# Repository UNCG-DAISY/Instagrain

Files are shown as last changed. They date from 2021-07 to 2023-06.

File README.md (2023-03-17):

# Instagrain

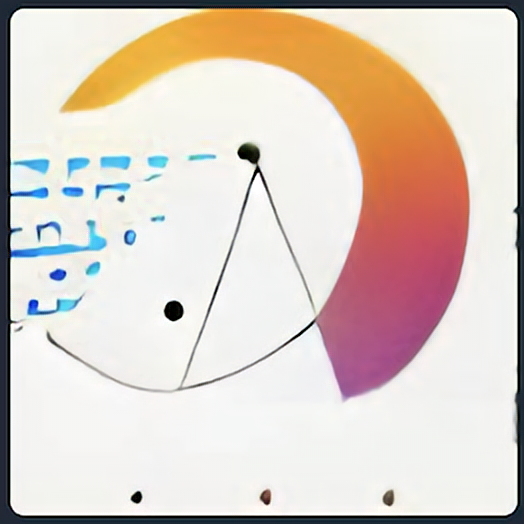
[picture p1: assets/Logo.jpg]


[](
https://github.com/UNCG-DAISY/SandCam/commits/main)












A camera for measuring sediment grain size in the field - ['instant grainification'](https://ui.adsabs.harvard.edu/abs/2007AGUFM.H51I0899R/abstract) (h/t Rubin & Chezar, 2007)
The camera currently runs a deep learning model to estimate grain size from pictures (using tensorflow lite)

We have several working prototypes out in the field. Here at HQ we continue to refine the camera design, hardware, software, and ML model. 

Prototype 1 (3D printed case)

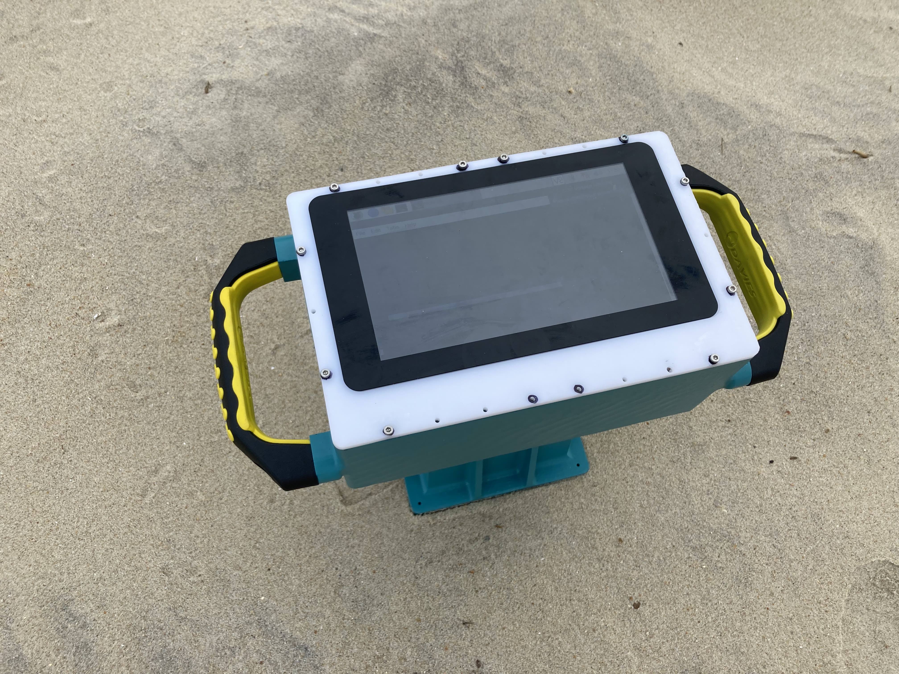
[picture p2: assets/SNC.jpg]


Prototype 2 (current version; CNC'ed case and 3D printed parts)

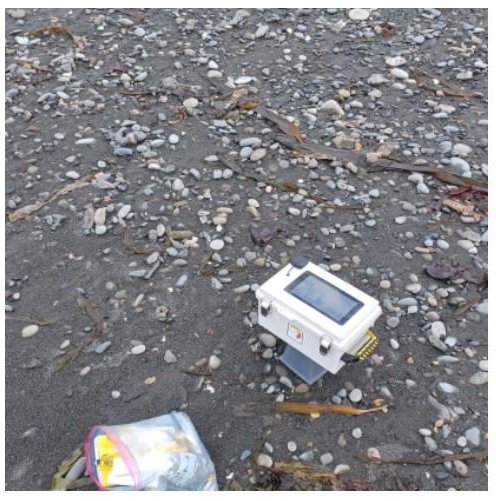
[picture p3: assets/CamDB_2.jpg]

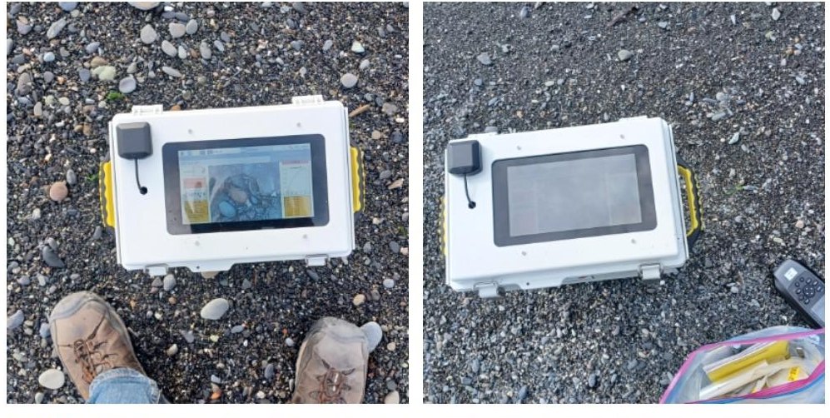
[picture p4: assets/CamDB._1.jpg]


## Do you want to be involved?:

0. Get in touch with us, we would be happy to collaborate!

1. Check out our [wiki](https://github.com/UNCG-DAISY/Instagrain/wiki) to learn how to build and use the camera.  

2. Read through the repository to look at the files/code we provide.

3. Check out the open [issues](https://github.com/UNCG-DAISY/Instagrain/issues) and participate in our [discussion](https://github.com/UNCG-DAISY/Instagrain/discussions). 

## Code of Conduct:

We intend to foster an inclusive and respectful environment surrounding the contribution and discussion of our project. Make sure you understand our [Code of Conduct](./CODE_OF_CONDUCT.md).

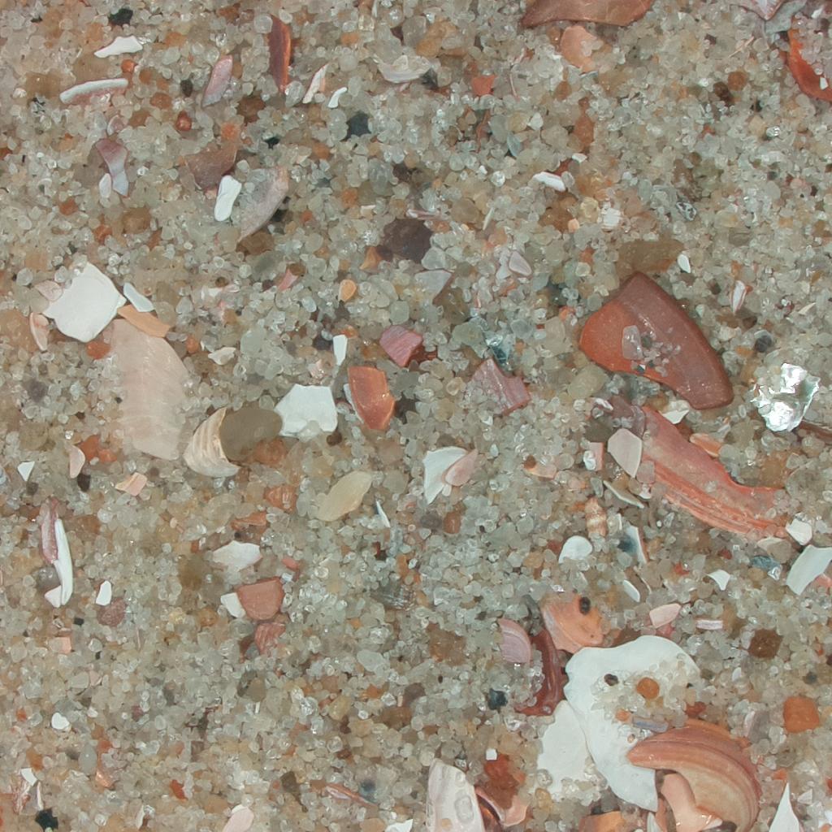
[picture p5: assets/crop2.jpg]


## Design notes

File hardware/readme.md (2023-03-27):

# This is the hardware folder

** please refer to the Wiki for instructions on how to build the device **

There are multiple versions of both the camera case and the electronics/hardware.

V1: The Case is fully 3d printed. We strongly recommend using an SLA printer. We have verified this model works with a FormLab 3+ using grey pro resin.

V2: This new case is a custom CNC'ed polycase enclosure and a few 3D printed parts. Again we recommend an SLA printer (we used a Formlab 3/3+ and Grey pro resin), but have heard of success using an FDM printer. There are mounting holes for an (optional) Google Coral edgeTPU, the GPS is provided by an Adafruit GPS hat connected to an external antenna (via an adaptor). 

V3: A smaller custom CNC'ed polycase enclosure, with fewer mounting points, and iterating on some design choices. Again there are a few 3D printed parts, and we recommend an SLA printer (we used a Formlab 3/3+ and Grey pro resin), but have heard of success using an FDM printer. The mounting holes for the Google Coral edgeTPU are eliminated, we switched to a USB GPS to simplify the BOM/parts list.

Notes:
- All `.stp` files can be viewed using [Autodesk Viewer](https://viewer.autodesk.com)
- The camera tent is interchangeable between V2 and V3, as is the ring light holder. (but the screen brackets are different between V2 and V3)

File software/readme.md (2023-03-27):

# This is the software folder

** please refer to the Wiki for instructions on how to set up the software on the device **

There are multiple versions of the case and hardware for hte camera, and we provide here matching versions of the software for each hardware configuration.

The software for the v1 and v2 camera are in the the `v2_and_v1` folder. This is software for the fully 3D printed camera and the larger (v2) custom CNC'ed polycase enclosure. This runs on Raspbian 'Buster', and uses Picamera 

The software for the v3 camera (smaller polycase enclosure) is provided in the `v3` folder. This runs on Raspbian 'Buster', and uses the Picamera library.

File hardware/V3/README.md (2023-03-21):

# Camera hardware readme for v3

** please note that there are multiple versions of both the camera case and the electronics/hardware. **

You are looking at V3, where the case is a smaller custom CNC'ed polycase enclosure and a few 3D printed parts. We recommend an SLA printer (we used a Formlab 3/3+ and Grey pro resin), but have heard of success using an FDM printer. 

### BOM v3

Full List of Materials can be found on the BOMv3.csv, (currently a rough draft)

---
### Major Components

- Most of the major Components can be ordered from our Adafruit wishlist http://www.adafruit.com/wishlists/561634 additionally there is Digikey links available in the [`BOMv3.csv`]  
  - The recommended microSD card can be bought on Amazon https://www.amazon.com/SanDisk-Extreme-microSDHC-UHS-3-SDSQXAF-032G-GN6MA/dp/B06XWMQ81P/
  - Due to chip shortages in 2021 and 2022, the Raspberry Pi 4 may not be available on Adafruit
- There are two STEP files that can be sent to Polycase* to order the custom-designed, CNC-machined camera housing (expect 1 to 3 week lead time). Polycase should alread have the "setup" complete, which reduces the overall unit cost. 
  - WQ-50_BODY.step
  - WQ-50_LID.stp
  - WQ-50_BASEPLATE.stp

*Instructions for sending requests for custom CNC-machined parts are available at https://www.polycase.com/customized-enclosures 

---
### Hardware

The fastener hardware can be ordered from a Mcmaster-Carr cart https://www.mcmaster.com/order/rcvRtedOrd.aspx?ordid=9740526925745&lnktyp=txt

---
### 3D Parts

There are four `.stl` files
- [`Camcover.stl`](./Camcover.stl)
- [`screenbracketsmaller.stl`](./screenbracketsmaller.stl)
- [`ledmountv2.stl`](./ledmountv2.stl)
- [`focuscover.stl`](./focuscover.stl)

We recommend printing all of them with a SLA printer with a build volumne of 14.5 × 14.5 × 18.5 cm and using grey pro resin.

Printing takes roughly 44.45hrs with a Form3/3+ printer (Look at [`BOMv3.csv`](./BOMv3.csv) for full part breakdown)

---

# Wiring Diagram

To assemble the camera, you will need the parts described in the bill of materials — [`BOMv3.csv`](./BOM.csv). 

A wiring diagram is available in Fritzing format — [`sandcamv2.fzz`](./sandcamv2.fzz).



---

# Build Instructions 

---

### Tools Needed 
- Soldering Iron
- Soldering Wire
- Flux
- Wire Strippers
- Metric Hex Bit Set
- Imperial Allen Key Set

### Components 
The Build Process is Broke down into 8 major parts:
- Soldering the Adafruit Ultimate GPS Hat and Neopixel board
- Mounting the Screen 
- Camera Assembly 
- Installing Handles
- Base Plate Assembly 
- Final assembly
- Focusing the Camera

---

 ### Step 1 --- Soldering 
First solder the GPIO header to the Adafruit ultimate GPS hat  


Next cut three, 8in male to female jumper cables in half, red for 5v, black for ground, and purple for data  
  

Once the wires are cut strip off about 5mm from each wire similar to how it is done in the above picture
and then twist the ends of the wires together and tin them  

 
Now we will solder the female ends to the Neopixel board, make sure solder the red wire to the middle 5v, the black wire to the middle GND, and the purple wire to the data input, so that the [`ledmountv2.stl`](./ledmountv2.stl) fits 


Next solder the male ends to the Adafruit Ulimate GPS Hat, the red wire to the 5v strip, the black to the GND strip, and the purple wire to GPIO #8 
Tip: I recommend soldering the 5v and GND at different ends (Differenly then I did in the picture below)



For the final step place the Neopixel Light into the [`ledmountv2.stl`](./ledmountv2.stl) 


---

### Step 2 --- Mounting the Screen
For this step, four 8mm M3 socket head screws, four 12mm M2.5 socket head screws, and four M2.5 hex nuts are needed
First start the four M3 Socket Head Screws into the two mounting holes in the center of the [`screenbracket.stl`](./screenbracket.stl) 
(will have a picture here soon)

Next attach the Brackets to the polycase with the four 12mm M2.5 socket head screws and the four M2.5 hex nuts



Once attached place the screen face down with the larger bezel on the left 


Finish by putting the outside of the polycase lid to the backside of the Screen and tightem the M3 socket head screws to the screen till the screen is flush with the front of the polycase  



---

### Step 3 --- Mounting the Coral TPU
Mounting the Coral TPU uses four 10mm M2.5 female to female hex standoffs, four 12mm M2.5 socket head screws, and four 6mm M2.5 socket head screws  
This is a fairly starightforward step, for now we recommend it is mounted on the outside until tempature testing can be done with the Coral TPU on the inside


### Step 4 --- Camera Assembly
For this step you will need eight 16mm female to male standoffs, four 2.5mm hex nuts, and four 6mm M2.5 socket head screws  
For the purpose of focusing the Pi HD camera you will need to disassemble and remove this part

The removed part and pi HD camera will now look like this

Next attach 4 standoffs to the bottom of the camera and then 4 between the neopixel light and the top of the pi camera



Finally attach the the camera to the outside of the case with the four 6mm M2.5 socket head bolts



---

### Step 5 --- Mounting the Handles
For this step you will need four quarter inch bolts and four quarter inch lock nuts  




---

### Step 6 --- Base Plate Assembly
For this step you will need two ribbon cables, four 10mm female to male standoffs, four 11mm female to male standoffs, a velcro strap, four M2.5 hex nuts, and four 6mm M2.5 socket head screws     
First step is to attach the two ribbon cables to the Raspi, for the screen and the camera  


Next attach the adafruit ultimate GPS hat with the black 11mm standoffs, then attach the 10mm standoffs to the bottom of the pi    



Secure the Raspi assembly to the baseplate with the four 6mm M2.5 socket head screws, and then secure the battery to the baseplate with the velcro strip


Finally secure the baseplate in the bottom of the case with the four screws that come with the polycase


---

### Step 7 --- Final Assembly
Thread the GPS antenna through the hexagonal hole in the front of the case annd attach wih double sided tape or glue to the outside of the case   


Next pull the camera ribbon through the slotted hole in the bottom of the case, and then connect the jumper cables


Connect the ground and 5v jumper cable to the screen, and connect the display ribbon to the screen


Connect the GPS to the adafruit ultimate GPS hat and zip tie in place to secure



For the final step plug in the battery to the on/off button, the on/off button to the Raspi, and then the coral TPU to the Pi


---

### Step 8 --- Focusing the Camera 
This is by far the hardest step, it is recommended to disconnect the screen and plug the raspi into a larger screen via hdmi   
First remove the [`Camcover.stl`](./Camcover.stl) and attach the [`focuscover.stl`](./focuscover.stl) which allows for better access to the camera 
Boot up the raspi and run the [`preview.py`](./preview.py) script
Focus the camera by twisting the HD lens  (this step might take a while), it is recommened to keep a small apeture for a large depth of focus  
Once the camera is in focus tighten down all the camera screws and place the [`Camcover.stl`](./Camcover.stl) on the case by inserting the pegs and twisting

Finally the touch screen can be hooked back up and the Sandcam is now ready to work
(pictures coming soon)

---

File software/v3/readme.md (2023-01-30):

# Setting up the camera software on the Pi

After assembling the case and wiring the electronics for the RPi (see the ['hardware directory'](../hardware)), it's time to get the Software and configurations set.

By default the camera runs a deep learning model, but can also run [pyDGS](https://github.com/dbuscombe-usgs/pyDGS) — software written by [Dan Buscombe](https://github.com/dbuscombe-usgs) that estimates grain size distribution (percent finer) of an image using the continuous wavelet transform.

## Option 1
Flash sd card with image from https://cshl.synology.me:5001/d/f/670216654824718296   

## Option 2
## Update Pi 

Boot up Raspberry Pi and connect to internet, and update Raspberry Pi with commands
```
sudo apt-get update
sudo apt-get upgrade
sudo reboot
```

## Configure Pi

Applications menu -> Preferences -> Raspberry Pi Configuration -> Interfaces -> ENABLE; Camera, SPI,(SSH, VNC are optional)  
`sudo reboot` 

## Add Hardware

After reboot  
Power Raspi off and add header extension, attach GPS to UART pins. Place RTC on I2C.
Connect Pi HQ camera to raspberry pi  

Connect Button to GPIO26 and to GND 
Connect LED light to GPIO18, 5v (back of RTC), and GND  
Power Raspberry pi on   

## Install the Pandas Package   
`pip3 install pandas`   

## Install the MatPlotLib Package
`sudo pip3 install maplotlib`

## Install scipy
`sudo apt-get install libatlas-base-dev`

`pip3 install scipy`

## set up GPS

`sudo raspi-config`    
interfacing options (3) -> Serial Port (P6) -> No -> Yes -> Finish   
then reboot   

Install, gpsd, gpsmon and cgps  
`sudo apt-get install gpsd-clients gpsd -y`

config GPS to work with correct serial device  
`sudo nano /etc/default/gpsd`  
Look for  `DEVICES=""`  
Change to `DEVICES="/dev/serial0"`  
Now save file (control X, Y) 
`pip3 install gpsd-py3` to download gps for python3


## set up RTC

`sudo raspi-config` Interface options (3) -> (P5) I2C -> yes -> finish  




  
`sudo reboot`  
Now use i2cdetect to see if the RTC is working   
`sudo i2cdetect -y 1` will show mounted drives, you should see a 68  
  
`sudo nano /boot/config.txt`        
Add to the end    
`#rtc`   
`dtoverlay=i2c-rtc,ds3231`     
save and exit (control x, y, enter)   
  
Now that we have the RTC ready to work on boot, restart your pi and..
`sudo i2cdetect -y 1` a mounted drive will have a "UU" ID  
   
Setting up RTC to be the main clock  
First disable the fake "hwclock"   
`sudo apt-get -y remove fake-hwclock`   
`sudo update-rc.d -f fake-hwclock remove`      
`sudo systemctl disable fake-hwclock`     

Second make the RTC to the main clock   
Run `sudo nano /lib/udev/hwclock-set` and comment out the following lines with `#`   
`if [-e/run/systemd/system];then`   
`exit 0`    
`fi`     
   
`/sbin/hwclock --rtc=$dev --systz --badyear`   

`/sbin/hwclock --rtc=$dev --systz`   
    

Make sure there is an internet connection so that the clocks can sync

## set up Neopixel Lite   
`sudo pip3 install rpi_ws281x adafruit-circuitpython-neopixel`   

## set up Tensorflow Lite

Follow instructions to `pip install` the tflite runtime on the Raspberry Pi
https://www.tensorflow.org/lite/guide/python

create a `/models/` directory on the desktop and place the `*.tflite` file (the tflite model) in that directory.

## set up Google Coral TPU (Optional)  
Run the commands   
`echo "deb https://packages.cloud.google.com/apt coral-edgetpu-stable main" | sudo tee /etc/apt/sources.list.d/coral-edgetpu.list`   
`curl https://packages.cloud.google.com/apt/doc/apt-key.gpg | sudo apt-key add -`   
`sudo apt-get update`   

Next Install Edge TPU Runtime
`sudo apt-get install libedgetpu1-std`   

Now Install the Pycoral Library   
`sudo apt-get install python3-pycoral`   

The Google Coral is ready to be plugged in now  
To test use the code below   
`mkdir coral && cd coral`   
`git clone https://github.com/google-coral/pycoral.git`   
`cd pycoral`   

`bash examples/install_requirements.sh classify_image.py`   

`python3 examples/classify_image.py \`  
`--model test_data/mobilenet_v2_1.0_224_inat_bird_quant_edgetpu.tflite \`  
`--labels test_data/inat_bird_labels.txt \`  
`--input test_data/parrot.jpg` 

The outtput should look something like the screenshot below, if it is not working restart Pi and try this section again, it has been finicky for me



## set up pyDGS (optional)
visit https://github.com/dbuscombe-usgs/pyDGS to look pyDGS or download to pi with `git clone --depth 1 https://github.com/dbuscombe-usgs/pyDGS.git`  
once downloaded edit test.py script to look like example code in SandCam --> camerasoftware --> pyDGS --> example_test.py  
next copy the __pycache__ folder, dgs.pyc, and dgs.py to your SandCam folder 

--- 

Helpful instructions to get packages for Ring LED, GPS, Coral TPU, and RTC  
https://www.thegeekpub.com/16187/controlling-ws2812b-leds-with-a-raspberry-pi/  
https://ozzmaker.com/berrygps-setup-guide-raspberry-pi/  
https://coral.ai/docs/accelerator/get-started#1-install-the-edge-tpu-runtime   
https://maker.pro/raspberry-pi/tutorial/how-to-add-an-rtc-module-to-raspberry-pi  

## Usage
When the Raspi is booted up, double click on the RUN.sh script  
Once the GUI is booted up you will see two buttons, preview and shutter  
Preview will show a live preview of the camera, make sure there is no large shells, sticks, or debry 
Photos and a text file will be stored in a new folder with the date and time, the text file will have every photo with the time taken, corresponding GPS coordinates, altitude, and grain size percentiles  

NOTE: -9999 under lat, lon, and alt means the GPS can not get a lock on coordinates. For best GPS results use external GPS.  

photos  
 
cropped photos  
  
Example text file  


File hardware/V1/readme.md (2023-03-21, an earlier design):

# Camera hardware readme for v1

** please note that there are multiple versions of both the camera case and the electronics/hardware. **

You are looking at V1, where the Case is fully 3d printed. We strongly recommend using an SLA printer. We have verified this model works with a FormLab 3+ using grey pro resin.

----

This directory addresses two aspects of the camera: 

- the 3D printed case of tha camera
- the electronic assembly of the camera. 

## 3D Printed case

There are 5 `.stl` files 

1. [Camera body](./body_sedicamsmallerv2.stl)
2. [Light mount](./lightmount.stl)
3. [Battery case](./battery_case.stl)
4. [Screen Mount](./screen_mount.stl)
5. [USB Door](./usbdoor_sedicam.stl)

We recommend printing all of them with a SLA printer with a build volumne of XXX and using rigid resin.

Printing takes roughly XXX with a XXX printer

Instructions for assembly are forthcoming.

---
# Wiring diagram 

To assemble the camera, you will need the parts described in the bill of materials — [`BOM.md`](./BOM.md). 

A wiring diagram is available in Fritzing format — [`SediNetCamv2.fzz`](./SediNetCamv2.fzz). 

Instructions for assembly are forthcoming.



---

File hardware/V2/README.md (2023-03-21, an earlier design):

# Camera hardware readme for v2

** please note that there are multiple versions of both the camera case and the electronics/hardware. **

You are looking at V2, where the case is a custom CNC'ed polycase enclosure and a few 3D printed parts. We recommend an SLA printer (we used a Formlab 3/3+ and Grey pro resin), but have heard of success using an FDM printer. 

# BOM v2

Full List of Materials can be found on the [`BOMv2.csv`](./BOMv2.csv)

---
### Major Components

- Most of the major Components can be ordered from our Adafruit wishlist http://www.adafruit.com/wishlists/543790 additionally there is Digikey links available in the [`BOMv2.csv`](./BOMv2.csv)
  - The Google Coral can be found at https://coral.ai/products/accelerator  
  - The recommended microSD card can be bought on Amazon https://www.amazon.com/SanDisk-Extreme-microSDHC-UHS-3-SDSQXAF-032G-GN6MA/dp/B06XWMQ81P/
  - Due to chip shortages in 2021 and 2022, the Raspberry Pi 4 may not be available on Adafruit
- There are two STEP files that can be sent to Polycase* to order the custom-designed, CNC-machined camera housing (expect 1 to 3 week lead time). Polycase should alread have the "setup" complete, which reduces the overall unit cost. 
  - WQ-57C_LID.stp
  - WQ-57_Body.stp

*Instructions for sending requests for custom CNC-machined parts are available at https://www.polycase.com/customized-enclosures 

---
### Hardware

The fastener hardware can be ordered from a Mcmaster-Carr cart https://www.mcmaster.com/order/rcvRtedOrd.aspx?ordid=2837271750220&lnktyp=txt 

---
### 3D Parts

There are four `.stl` files
- [`Camcover.stl`](./Camcover.stl)
- [`screenbracket.stl`](./screenbracket.stl)
- [`ledmountv2.stl`](./ledmountv2.stl)
- [`focuscover.stl`](./focuscover.stl)

We recommend printing all of them with a SLA printer with a build volumne of 14.5 × 14.5 × 18.5 cm and using rigid resin.

Printing takes roughly 44.45hrs with a Form3/3+ printer (Look at [`BOMv2.csv`](./BOMv2.csv) for full part breakdown)

---
### CNC Part

There is only one part that needs to be custom made or hand machined
- [`WQ-57P-01.pdf`](./WQ-57P-01.pdf)

The above file has all the necessary dimensions for hand machining, feel free to make any improvements and share!

---

# Wiring Diagram

To assemble the camera, you will need the parts described in the bill of materials — [`BOMv2.csv`](./BOM.csv). 

A wiring diagram is available in Fritzing format — [`sandcamv2.fzz`](./sandcamv2.fzz).



---

# Build Instructions 

---

### Tools Needed 
- Soldering Iron
- Soldering Wire
- Flux
- Wire Strippers
- Metric Hex Bit Set
- Imperial Allen Key Set

### Components 
The Build Process is Broke down into 8 major parts:
- Soldering the Adafruit Ultimate GPS Hat and Neopixel board
- Mounting the Screen
- Coral mounting 
- Camera Assembly 
- Installing Handles
- Base Plate Assembly 
- Final assembly
- Focusing the Camera

---

 ### Step 1 --- Soldering 
First solder the GPIO header to the Adafruit ultimate GPS hat  


Next cut three, 8in male to female jumper cables in half, red for 5v, black for ground, and purple for data  
  

Once the wires are cut strip off about 5mm from each wire similar to how it is done in the above picture
and then twist the ends of the wires together and tin them  

 
Now we will solder the female ends to the Neopixel board, make sure solder the red wire to the middle 5v, the black wire to the middle GND, and the purple wire to the data input, so that the [`ledmountv2.stl`](./ledmountv2.stl) fits 


Next solder the male ends to the Adafruit Ulimate GPS Hat, the red wire to the 5v strip, the black to the GND strip, and the purple wire to GPIO #8 
Tip: I recommend soldering the 5v and GND at different ends (Differenly then I did in the picture below)



For the final step place the Neopixel Light into the [`ledmountv2.stl`](./ledmountv2.stl) 


---

### Step 2 --- Mounting the Screen
For this step, four 8mm M3 socket head screws, four 12mm M2.5 socket head screws, and four M2.5 hex nuts are needed
First start the four M3 Socket Head Screws into the two mounting holes in the center of the [`screenbracket.stl`](./screenbracket.stl) 
(will have a picture here soon)

Next attach the Brackets to the polycase with the four 12mm M2.5 socket head screws and the four M2.5 hex nuts



Once attached place the screen face down with the larger bezel on the left 


Finish by putting the outside of the polycase lid to the backside of the Screen and tightem the M3 socket head screws to the screen till the screen is flush with the front of the polycase  



---

### Step 3 --- Mounting the Coral TPU
Mounting the Coral TPU uses four 10mm M2.5 female to female hex standoffs, four 12mm M2.5 socket head screws, and four 6mm M2.5 socket head screws  
This is a fairly starightforward step, for now we recommend it is mounted on the outside until tempature testing can be done with the Coral TPU on the inside


### Step 4 --- Camera Assembly
For this step you will need eight 16mm female to male standoffs, four 2.5mm hex nuts, and four 6mm M2.5 socket head screws  
For the purpose of focusing the Pi HD camera you will need to disassemble and remove this part

The removed part and pi HD camera will now look like this

Next attach 4 standoffs to the bottom of the camera and then 4 between the neopixel light and the top of the pi camera



Finally attach the the camera to the outside of the case with the four 6mm M2.5 socket head bolts



---

### Step 5 --- Mounting the Handles
For this step you will need four quarter inch bolts and four quarter inch lock nuts  




---

### Step 6 --- Base Plate Assembly
For this step you will need two ribbon cables, four 10mm female to male standoffs, four 11mm female to male standoffs, a velcro strap, four M2.5 hex nuts, and four 6mm M2.5 socket head screws     
First step is to attach the two ribbon cables to the Raspi, for the screen and the camera  


Next attach the adafruit ultimate GPS hat with the black 11mm standoffs, then attach the 10mm standoffs to the bottom of the pi    



Secure the Raspi assembly to the baseplate with the four 6mm M2.5 socket head screws, and then secure the battery to the baseplate with the velcro strip


Finally secure the baseplate in the bottom of the case with the four screws that come with the polycase


---

### Step 7 --- Final Assembly
Thread the GPS antenna through the hexagonal hole in the front of the case annd attach wih double sided tape or glue to the outside of the case   


Next pull the camera ribbon through the slotted hole in the bottom of the case, and then connect the jumper cables


Connect the ground and 5v jumper cable to the screen, and connect the display ribbon to the screen


Connect the GPS to the adafruit ultimate GPS hat and zip tie in place to secure



For the final step plug in the battery to the on/off button, the on/off button to the Raspi, and then the coral TPU to the Pi


---

### Step 8 --- Focusing the Camera 
This is by far the hardest step, it is recommended to disconnect the screen and plug the raspi into a larger screen via hdmi   
First remove the [`Camcover.stl`](./Camcover.stl) and attach the [`focuscover.stl`](./focuscover.stl) which allows for better access to the camera 
Boot up the raspi and run the [`preview.py`](./preview.py) script
Focus the camera by twisting the HD lens  (this step might take a while), it is recommened to keep a small apeture for a large depth of focus  
Once the camera is in focus tighten down all the camera screws and place the [`Camcover.stl`](./Camcover.stl) on the case by inserting the pegs and twisting

Finally the touch screen can be hooked back up and the Sandcam is now ready to work
(pictures coming soon)

---

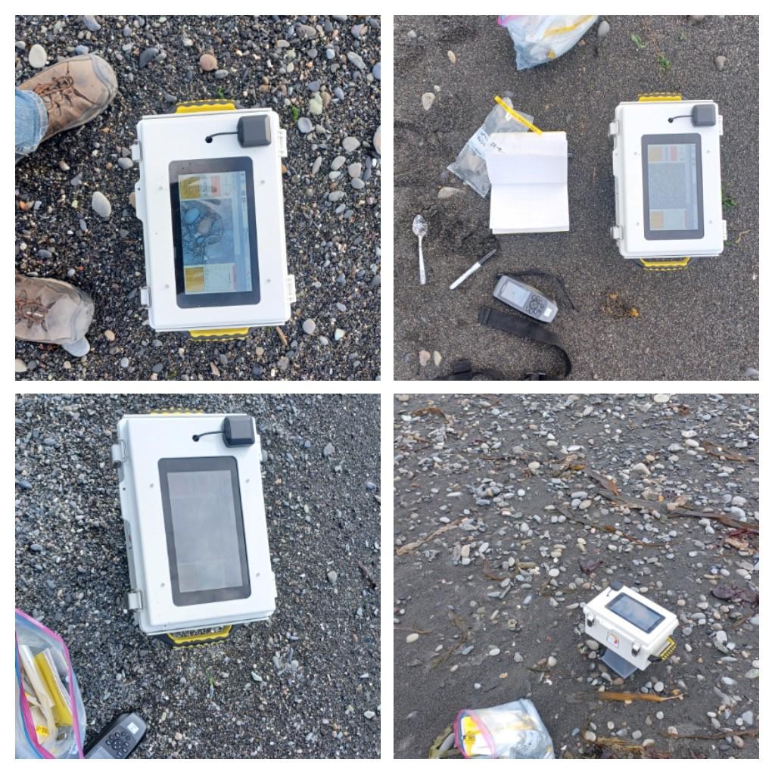
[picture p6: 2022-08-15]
assets/CamDB.jpg

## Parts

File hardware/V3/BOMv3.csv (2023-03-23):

OM SandCam V2
Major Components
Item | Price per Unit | Manufactuer | Procurment Type | ID Number | Link
Polycase WQ-50 (per unit, assuming order is 5 parts) | $133.65 | Polycase | CNC | NA | NA
Polycase WQ-50 Baseplate (per unit, assuming order is 5 parts) | $21.52 | Polycase | CNC | WQ-57P-01 | https://www.polycase.com/wq-50p
Raspberry Pi 4 Model B - 2 GB RAM | $45.00 | Adafruit | Off-The-Shelf | 4292 | https://www.adafruit.com/product/4292
SanDisk 32GB Micro SD card | $10.19 | Amazon | Off-The-Shelf | NA | https://www.amazon.com/SanDisk-Extreme-microSDHC-UHS-3-SDSQXAF-032G-GN6MA/dp/B06XWMQ81P |  |  | .
6mm 3MP Wide Angle Lens for Raspberry Pi HQ Camera - 3MP | $25.00 | Adafruit | Off-The-Shelf | 4563 | https://www.adafruit.com/product/4563
Raspberry Pi High Quality HQ Camera - 12MP | $50.00 | Adafruit | Off-The-Shelf | 4561 | https://www.adafruit.com/product/4561
USB Battery Pack for Raspberry Pi - 10000mAh - 2 x 5V outputs | $39.95 | Adafruit | Off-The-Shelf | 1566 | https://www.adafruit.com/product/1566
Pi Foundation Display - 7" Touchscreen Display for Raspberry Pi | $79.95 | Adafruit | Off-The-Shelf | 2718 | https://www.adafruit.com/product/2718
VK-162 G-Mouse - Remote Mount USB - External GPS Navigation Dongle | $19.99 | Amazon | Off-The-Shelf | NA | https://www.amazon.com/gp/product/B01EROIUEW
NeoPixel Ring - 24 x 5050 RGB LED with Integrated Drivers | $16.95 | Adafruit | Off-The-Shelf | 1586 | https://www.adafruit.com/product/1586
Total Component Costs | $442.20
3D printable Components
Item | Length | Width | Height | Recommended Printer | Recommended Resin | Volume/Print Time/Layers | Link
Camera Hood | 126mm | 126mm | 138.8mm | Form 3/3+ | Grey Pro | 310ml/30.5 hrs/1647 | https://github.com/UNCG-DAISY/SandCam/blob/main/hardware/V2/Camcover.stl
Screen Bracket | 140mm | 10mm | 12.6mm | Form 3/3+ | Grey Pro | 34.2ml/8.5 hrs/858 | https://github.com/UNCG-DAISY/SandCam/blob/main/hardware/V2/screenbracket.stl
LED Mount | 74mm | 74mm | 4mm | Form 3/3+ | Grey Pro | 9.74ml/5.45 hrs/659 | https://github.com/UNCG-DAISY/SandCam/blob/main/hardware/lightmount.stl
Focus Hood | 114mm | 114mm | 138.8mm | Form 3/3+ | Grey Pro | 46.44ml/14 hr/1472 | https://github.com/UNCG-DAISY/SandCam/blob/main/hardware/V2/focuscover.stl
Hardware
Item | Size | Length | Quantity | Unit of Measure | Unit Price | Total Cost | Manufacturer | Item Number | Webiste
18-8 Stainless Steel Socket Head Screw | M2.5 | 12mm | 8 | 1 pack of 100 each | $6.54 | $6.54 | McMaster-Carr | 91292A016
Stainless Steel Female Hex Standoff | M2.5 | 10mm | 4 | each | $1.32 | $5.28 | McMaster-Carr | 94868A165
Stainless Steel Male Hex Standoff | M2.5 | 16mm | 8 | each | $4.82 | $38.56 | McMaster-Carr | 93655A353
18-8 Stainless Steel Socket Head Screw | M2.5 | 6mm | 12 | 1 pack of 100 each | $6.00 | $6.00 | McMaster-Carr | 91292A010
18-8 Stainless Steel Socket Head Screw | M3 x 0.5mm | 8mm | 4 | 1 pack of 100 each | $5.45 | $5.45 | McMaster-Carr | 91292A112
18-8 Stainless Steel Socket Head Screw | 1/4" - 20 | 1.25" | 4 | 1 pack of 25 each | $17.51 | $17.51 | McMaster-Carr | 92196A544
Plastic Unthreaded-Hole Rectangular Pull Handle | 3-11/16 | NA | 2 | each | $4.24 | $8.48 | McMaster-Carr | 1078A311
Stainless Steel Male Hex Standoff | M2.5 | 10mm | 4 | each | $4.26 | $17.04 | McMaster-Carr | 93655A096
Brass M2.5 Standoffs for Pi HATs - Black Plated - Pack of 2 | M2.5 | 11mm | 4 | 1 pack of 2 each | $0.75 | $1.50 | AdaFruit | 2336 | https://www.adafruit.com/product/2336 | .
Female/Male Jumper Wires | NA | 6" | 5 | 20 | $1.95 | $1.95 | AdaFruit | 1954 | https://www.adafruit.com/product/1954
Metric 18-8 Stainless Steel Hex Nuts | M2.5 | NA | 12 | 1 pack of 100 each | $7.18 | $7.18 | McMaster-Carr | 91828A113
18-8 Stainless Steel Hex Nuts | 1/4" - 20 | NA | 4 | 1 pack of 100 each | $7.16 | $7.16 | McMaster-Carr | 91845A029
Long-Lasting Cable Ties | Narrow | 4" |  | 1 pack of 100 each | $8.60 | $8.60 | McMaster-Carr | 70215K61
316 Stainless Steel Washers | 1/4" | NA | 4 | 1 pack of 100 each | $10.01 | $10.01 | McMaster-Carr | 90107A029
18-8 Stainless Steel Washers | M2.5 | NA | 12 | 1 pack of 100 each | $2.86 | $2.86 | McMaster-Carr | 98689A111
20-inch camera ribbon | NA | 20" | 1 | 1 | $5.19 | $5.19 | Amazon | NA | https://www.amazon.com/dp/B07JZHD614/ref=cm_sw_r_apan_i_NXH4P163JZWWCMCC1P96
Fastening Cable Straps | NA | 8", 12" 18" | 2 or more | 1 pack of 20 each | $9.99 | $9.99 | Amazon | NA | https://www.amazon.com/dp/B071DGMNMX/ref=cm_sw_r_awdo_0EVQJTPBNCX9AGSSV8HP?th=1
Weather stripping | 1/4'' wide | 1/8'' thick | 532mm | 49 feet | $9.99 | $9.99 | Amazon | NA | https://www.amazon.com/dp/B0836Z1HN7/ref=cm_sw_r_apan_glt_i_WZYNVJH8T8CGN9EP6VX2
 |  |  |  |  | Total Hardware Costs | $142.20
TOTAL COST | ~$580
Adafruit Cart | http://www.adafruit.com/wishlists/561634
McMaster Cart | https://www.mcmaster.com/order/rcvRtedOrd.aspx?ordid=9740526925745&lnktyp=txt
Digikey Links
Raspberry Pi 4 Model B - 2 GB RAM |  |  |  |  |  |  |  |  | https://www.digikey.com/en/products/detail/raspberry-pi/Raspberry-Pi-4B-2GB/10258782
6mm 3MP Wide Angle Lens for Raspberry Pi HQ Camera - 3MP |  |  |  |  |  |  |  |  | https://www.digikey.com/en/products/detail/raspberry-pi/SC0124/12339169
Raspberry Pi High Quality HQ Camera - 12MP |  |  |  |  |  |  |  |  | https://www.digikey.com/en/products/detail/raspberry-pi/SC0818/12339164?s=N4IgTCBcDaIBYEcAEAHAlkgxgQwLYgF0BfIA
USB Battery Pack for Raspberry Pi |  |  |  |  |  |  |  |  | https://www.digikey.com/en/products/detail/adafruit-industries-llc/4288/10419640
Pi Foundation Display - 7" Touchscreen Display for Raspberry Pi |  |  |  |  |  |  |  |  | https://www.digikey.com/en/products/detail/raspberry-pi/8997466/6152806
NeoPixel Ring - 24 x 5050 RGB LED with Integrated Drivers |  |  |  |  |  |  |  |  | https://www.digikey.com/en/products/detail/adafruit-industries-llc/2863/5878438
Brass M2.5 Standoffs for Pi HAT |  |  |  |  |  |  |  |  | https://www.digikey.com/en/products/detail/raf-electronic-hardware/M2106-2545-SS/7681085
Female/Male Jumper Wires |  |  |  |  |  |  |  |  | https://www.digikey.com/en/products/detail/adafruit-industries-llc/1954/6827087

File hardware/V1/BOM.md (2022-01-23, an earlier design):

## Bill Of Materials for the camera

RPi Model 4 - (many places)

Powerbank — (our discussion here: https://github.com/UNCG-DAISY/SandCam/issues/43)

HQ picam lens - https://www.adafruit.com/product/4563

HQ picam - https://www.adafruit.com/product/4561

Touch display - https://www.amazon.com/Raspberry-Pi-7-Touchscreen-Display/dp/B0153R2A9I/

pi RTC - https://www.adafruit.com/product/4282

RTC battery - https://www.amazon.com/Energizer-CR1220-Drain-lithuim-Battery/dp/B003CU3E2Q

GPS - https://www.amazon.com/BerryGPS-IMUv3-Raspberry-Accelerometer-Magnetometer-Barometric/dp/B072MNBC9M
(we will also try this one: https://www.adafruit.com/product/2324)

GPS attenna - https://www.amazon.com/Bingfu-Waterproof-Navigation-Connector-Tracking/dp/B07R7RC96G/

shutter button - https://www.amazon.com/TWTADE-Momentary-Button-Normally-PBS-110-X-BK/dp/B07X3RRG37

on/off button - https://www.amazon.com/dp/B075YV8KTG/

other buttons to test: (https://www.amazon.com/OFNMY-Waterproof-Momentary-Button-PBS-33B/dp/B07NX7S8LV)

LED Ring Light - https://www.amazon.com/gp/product/B0774JNSCF

Standoffs - https://www.amazon.com/DYWISHKEY-Pieces-Female-Standoff-Assortment/dp/B07MW5P8JH/

Handles - https://www.mcmaster.com/handles/pull-handles-and-knobs/choose-a-color-unthreaded-hole-pull-handles/

female terminal - https://www.amazon.com/dp/B07VWD929M/

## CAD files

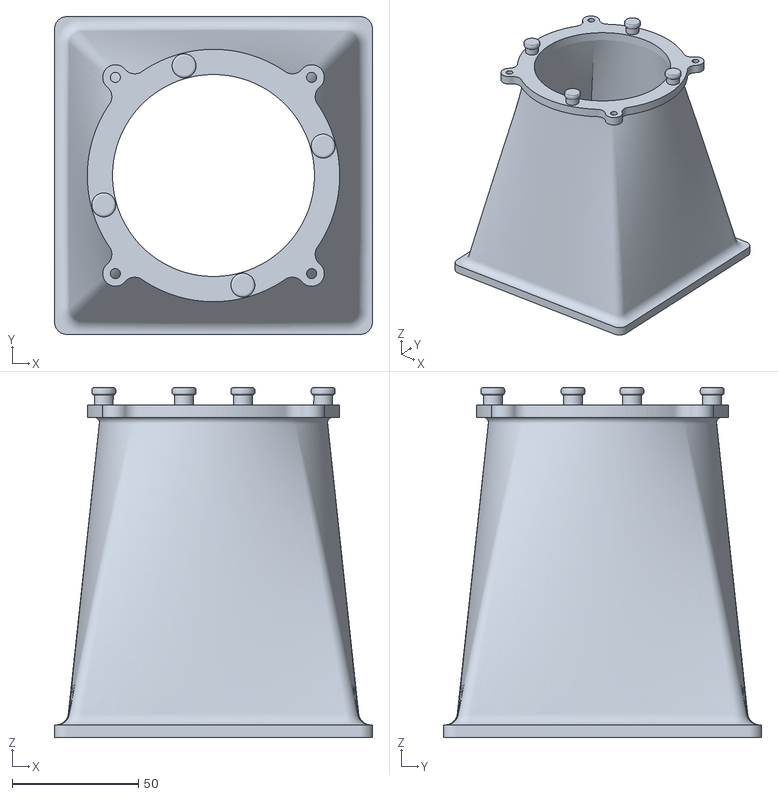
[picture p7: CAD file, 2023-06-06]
hardware/V3/cam_cover.stl
126.0 x 126.0 x 138.7

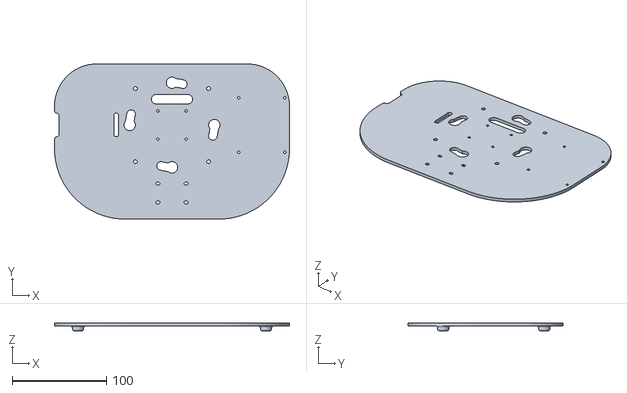
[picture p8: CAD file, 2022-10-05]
utilities/dev_platev2.stl
250.0 x 165.0 x 8.20

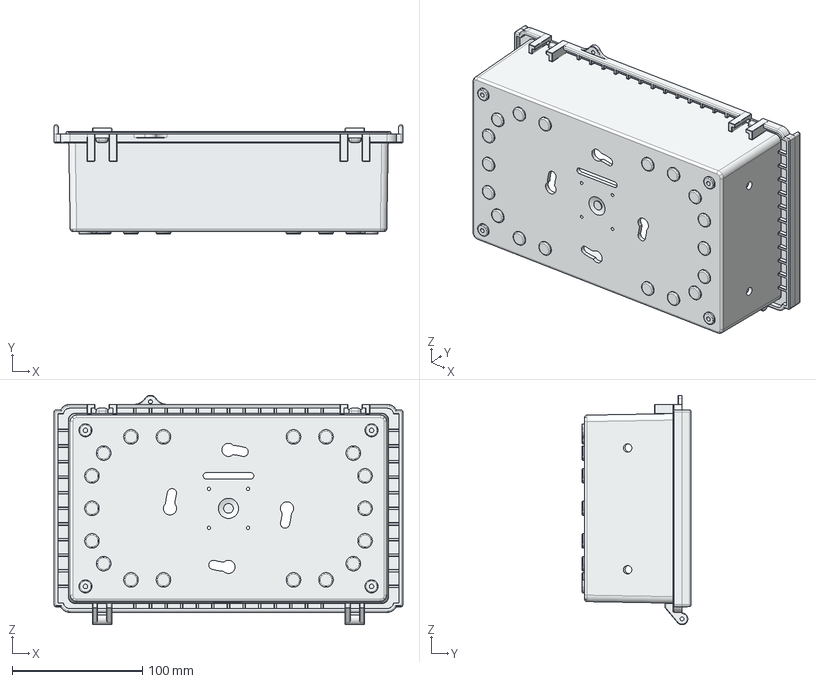
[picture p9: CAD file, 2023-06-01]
hardware/V3/WQ-50_BODY.stp
268.4 x 84.0 x 176.5 mm

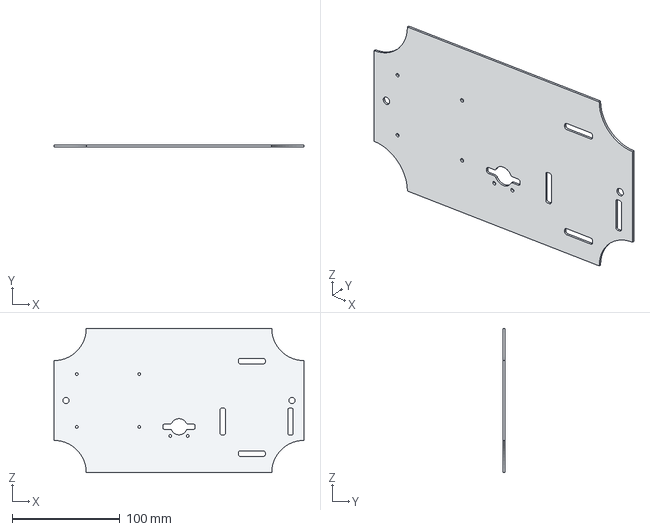
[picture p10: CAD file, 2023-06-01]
hardware/V3/WQ-50P_BASEPLATE.stp
232.4 x 1.60 x 134.1 mm

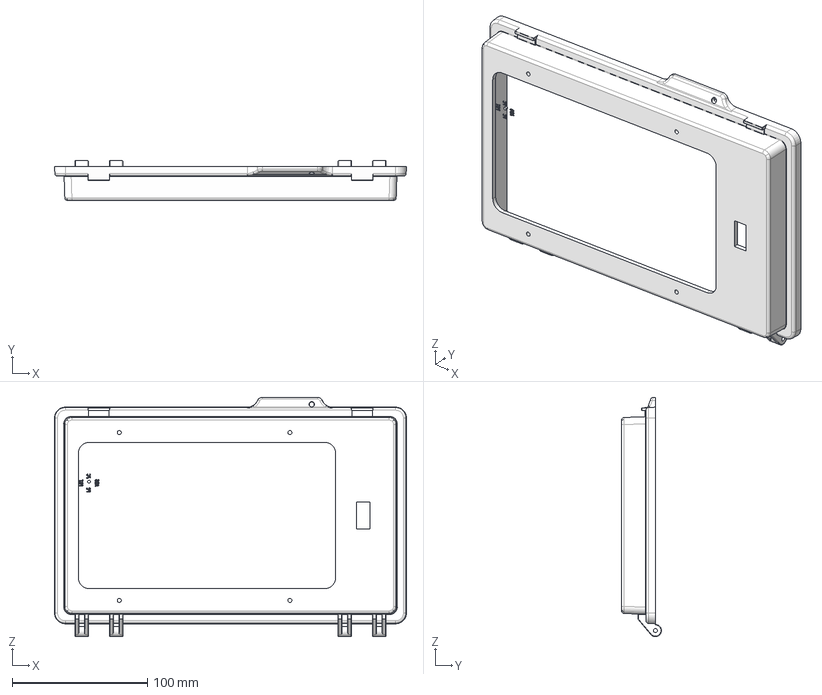
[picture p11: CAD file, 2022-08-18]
hardware/V3/WQ-50_LID.stp
260.0 x 29.5 x 176.7 mm

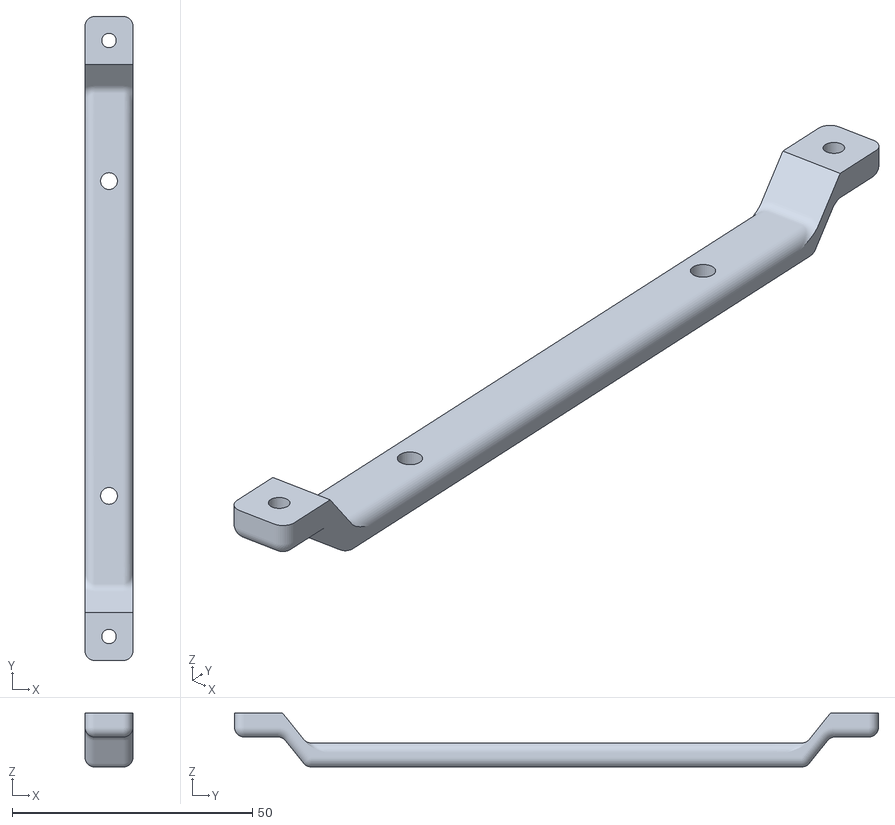
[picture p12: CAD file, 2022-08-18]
hardware/V3/screenbracketsmall.stl
10.0 x 134.0 x 11.2

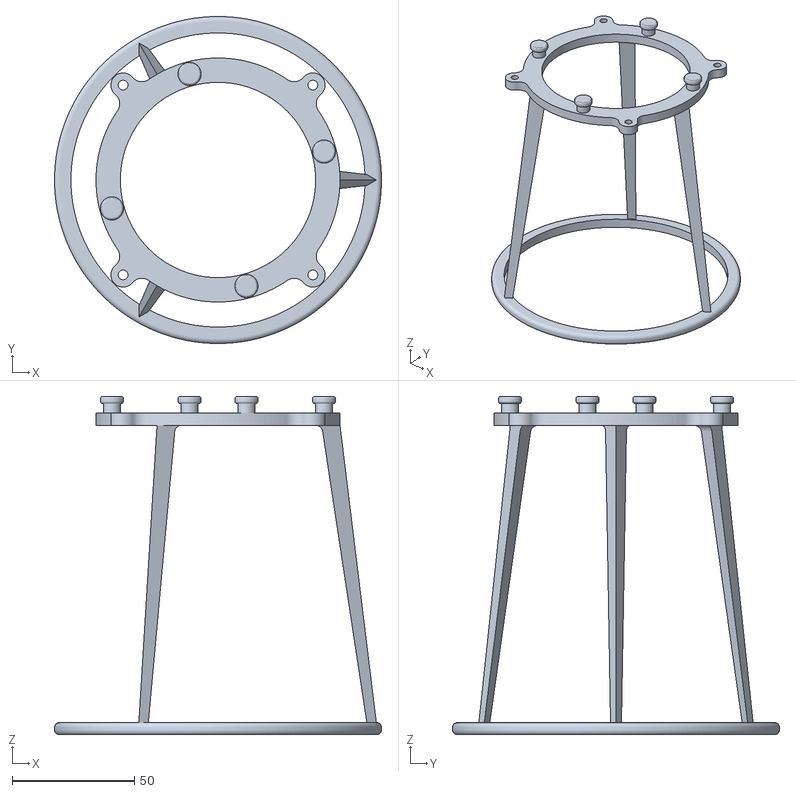
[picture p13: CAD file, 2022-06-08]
hardware/V3/focuscover.stl
134.0 x 134.0 x 138.7

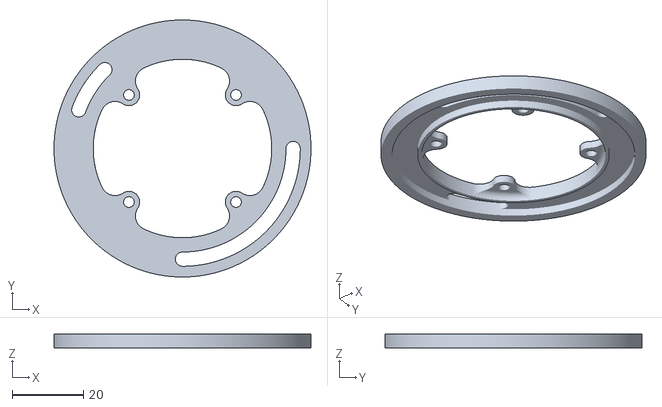
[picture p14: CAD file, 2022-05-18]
hardware/V3/ledmountv2.stl
72.0 x 72.0 x 4.00

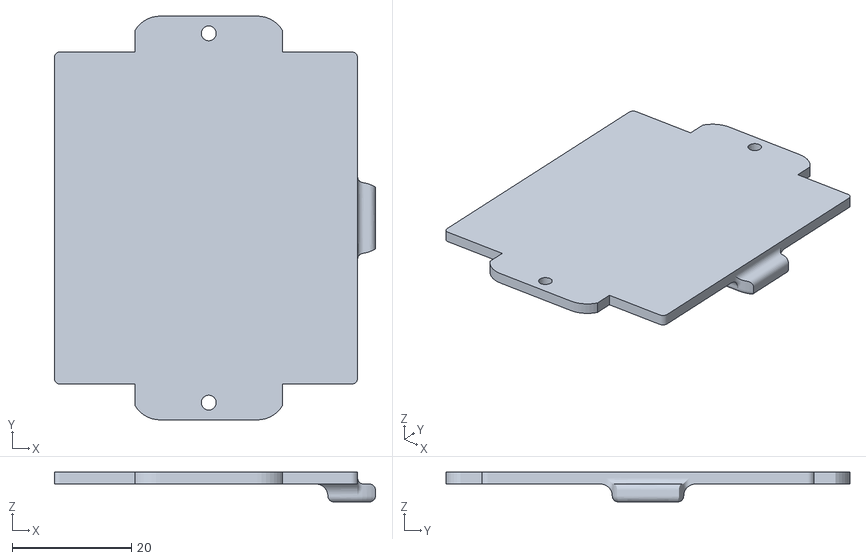
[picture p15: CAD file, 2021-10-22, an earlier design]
hardware/V1/usbdoor_sedicam.stl
53.9 x 67.8 x 5.00

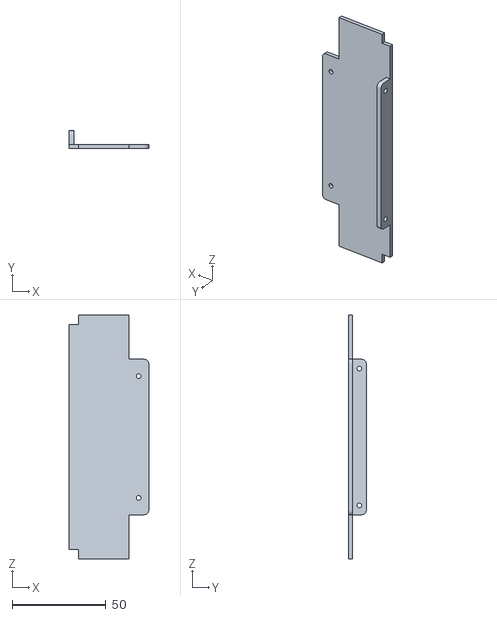
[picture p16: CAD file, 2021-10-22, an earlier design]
hardware/V1/battery_case.stl
42.5 x 9.45 x 130.0

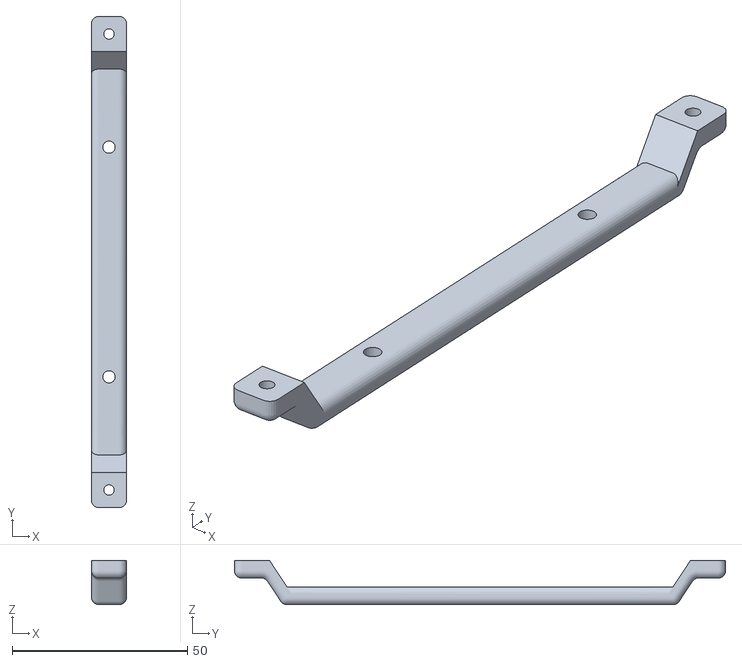
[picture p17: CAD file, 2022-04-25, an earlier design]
hardware/V2/screenbracket.stl
10.0 x 140.0 x 12.6

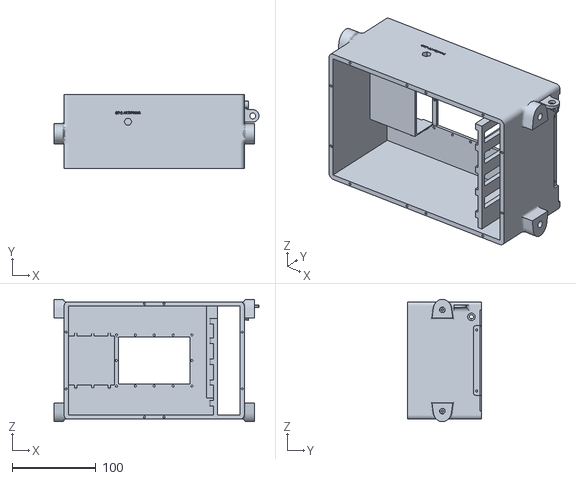
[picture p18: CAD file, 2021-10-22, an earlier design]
hardware/V1/body_sedicamsmallerv2.stl
244.5 x 88.2 x 146.1

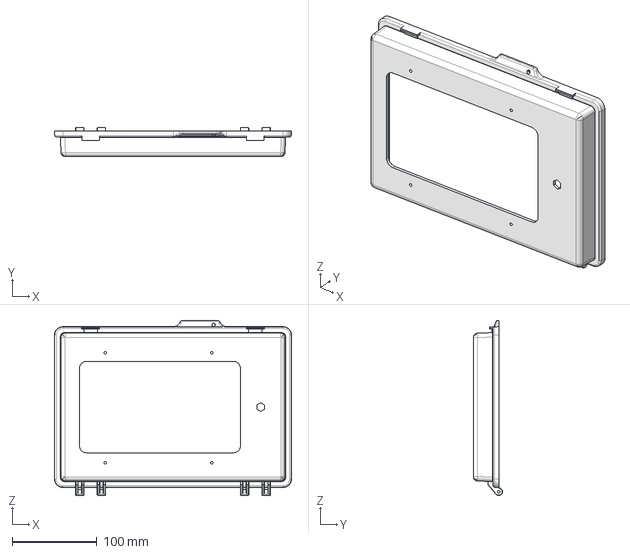
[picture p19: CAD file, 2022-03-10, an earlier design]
hardware/V2/WQ-57C_LID.stp
280.0 x 34.5 x 206.8 mm

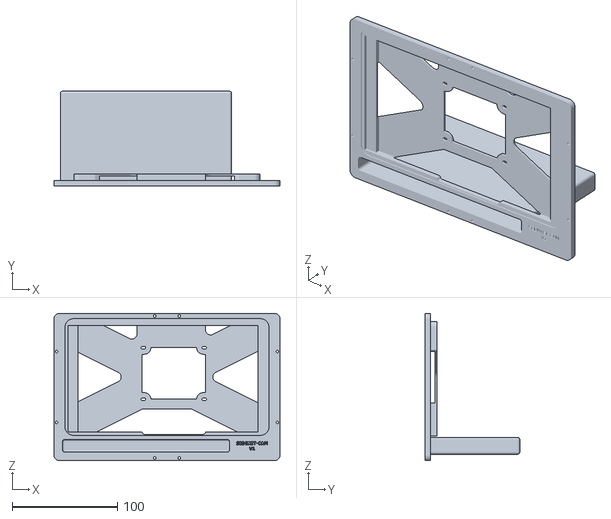
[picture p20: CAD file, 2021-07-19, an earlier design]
hardware/V1/screen_mount.stl
215.0 x 90.0 x 140.0

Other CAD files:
hardware/V2/Camcover.stl
hardware/V2/WQ-57_Body.stp

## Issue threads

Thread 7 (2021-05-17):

UNCG-DAISY/Instagrain #7: determine best distance from the bed for camera

ebgoldstein, 2021-05-17:
this will be determined via back and forth with the seidnet model

ebgoldstein, 2021-05-17:
from @jacobstasiewicz:
I took 3 pictures of a camera calibration board from 3 different distances to calculate pixel per inch. The results are as follows:
distance: 4 7/8 has a PPI of 624.38
distance: 3 1/2 in has a PPI of 858.52
distance: 2 1/2 in has a PPI of 1144.69

jacobstasiewicz, 2021-05-19:
Ordered tripod to take precise pictures at different elevations and run through SediNet

jacobstasiewicz, 2021-05-25:
Took 15 pictures at varying heights from 3 inches to 7 inches above the bed to run through sedinet model

jacobstasiewicz, 2021-05-25:
Cropped all pictures to 512 x 512 for sedinet model

jacobstasiewicz, 2021-05-26:
did calculations on lens angle to find pixels per mm

jacobstasiewicz, 2021-06-29:
found to be 3in

closed 2021-06-29 by jacobstasiewicz

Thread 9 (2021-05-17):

UNCG-DAISY/Instagrain #9: boot to camera

ebgoldstein, 2021-05-17:
write a script so that, upon startup, open the camera.

put scripts in the public github repository (`/camerasoftware` directory).

jacobstasiewicz, 2021-06-04:
Somewhat got it to work, still having issues on pulling up terminal to specify folder

ebgoldstein, 2021-10-07:
@jacobstasiewicz — are you ok if i write some code (via `cron`) so that the shell script runs as soon as the camera is booted?

jacobstasiewicz, 2021-10-07:
Yes I am, although I couldn't get the script to run via cron

ebgoldstein, 2021-10-07:
i will try, and likely fail...

ebgoldstein, 2021-10-14:
I did not try yet. in many ways the its fine at this stage if the users need to double tap the shell script to make the camera run.. i say this because debugigng is easier if the script does not run immediately

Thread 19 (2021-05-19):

UNCG-DAISY/Instagrain #19: Contact Dan Buscombe

jacobstasiewicz, 2021-05-19:
to discuss lighting options for camera and how to format spreadsheet for SediNet

ebgoldstein, 2021-05-21:
LED rings as far back as possible. very diffused light. as uniform as possible 

avoid specular reflections with light too close to the lens, and internal reflections.

ebgoldstein, 2021-05-21:
the P is Pixel, D is grain size...  so D50 is grain size in mm P50 is grain size in pixels... to convert just do mm/pixels..

jacobstasiewicz, 2021-05-21:
So how would I convert our sieved samples to grain size in pixels? I am a little confused now

ebgoldstein, 2021-05-21:
The idea is that each of these images from sedinet is from a sieve analysis, grains that make it through the upper sieve, but not the lower sieve. Each sample has a range of grain sizes. D5, D10, D50, etc. 

Images of these samples are taken, and the pixel dimension are determined.. so X mm/ pixel.. Then all teh grain size metrics are converted to Pixel Size metrics (P5, P10, P50, etc.)...  by dividing grain size metric (mm) by known pixel size (mm/pixel). 

that is what is expressed in these CSVs... does that make sense? so the steps for us would be:

- determine grain size metrics for a given sand sample
- take a picture of the sample
- compute pixel size of image
- convert the grain sizes metrics for the sample in 'P' metrics by dividing by the  pixel size.

closed 2021-05-24 by ebgoldstein

jacobstasiewicz, 2021-05-24:
Okay, I think I might of sent Dan an email before I saw you posted this but it clears everything up. So after I have done all of the pictures, computed pixel size and converted metrics to pixel size, I should be able to run it through the SediNet

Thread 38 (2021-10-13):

UNCG-DAISY/Instagrain #38: GPS does not always work in the field...

ebgoldstein, 2021-10-13:
The GPS does not always provide a location, and i was having some issues with exceptions..

I adjusted the script slightly so -9999 is the default and new values write on top (i will link my commit to this issue), but i am not sure that `gps.next()` is the best way to make sure a position is returned... 
i know this is an old S.O. thread, but i wonder if it hints at a way to deal with it... https://stackoverflow.com/questions/6146131/python-gps-module-reading-latest-gps-data

jacobstasiewicz, 2021-10-18:
Ill give this a look when I get the camera back

ebgoldstein, 2022-02-03:
we are switching the GPS to https://www.adafruit.com/product/2324, 

which has a tutorial here: https://learn.adafruit.com/adafruit-ultimate-gps-hat-for-raspberry-pi/

jacobstasiewicz, 2022-03-10:
GPS working reliably now with gpsd package. Tested with and without fix

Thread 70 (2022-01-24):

UNCG-DAISY/Instagrain #70: SD card image.

ebgoldstein, 2022-01-24:
probably the easiest way to reproducibly build/package the camera software is to provide an SD card image.. Then users could just have all the dependencies installed -i.e., they would just use balena etcher and everything would just work on the pi when they inserted the sd card..

 we could save the image on a zenodo repository, and link it here..

https://www.tomshardware.com/amp/how-to/back-up-raspberry-pi-as-disk-image

jacobstasiewicz, 2022-01-24:
Hey Evan I agree, good idea. After we speak tomorrow I can get on that

jacobstasiewicz, 2022-02-02:
Imaged a new sd card succesfully, both work. Now I am working on creating an image to update to a zenodo repo

jacobstasiewicz, 2022-02-15:
Uploaded to syno drive at https://cshl.synology.me:5001/d/f/670216654824718296

closed 2022-02-15 by jacobstasiewicz

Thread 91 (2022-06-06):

UNCG-DAISY/Instagrain #91: RTC woes..

ebgoldstein, 2022-06-06:
I think the instructions for the RTC are not correct.. i can work on this

ebgoldstein, 2022-06-09:
https://forums.adafruit.com/viewtopic.php?f=50&t=182292&p=885900&hilit=gps+hat+rtc#p885900

jacobstasiewicz, 2022-06-13:
The csv file is now updated from the gps in UTC, but it would still be nice to figure out the RTC

ebgoldstein, 2022-06-13:
let's keep this open, and i can rename this issue

ebgoldstein, 2022-06-20:
new rtc has been ordered.. this would mean swapping out {GPS hat+connector+antenna} for {RTC + USB-GPS).. this would require a bigger hole on the top case (for USB cable).

ebgoldstein, 2022-08-24:
I think this is not needed anymore with the RTC in V3, the GPS time recorded in the sample spreadsheet, and the 5 digit hash code being used for the folder name

closed 2022-10-12 by ebgoldstein

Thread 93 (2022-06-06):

UNCG-DAISY/Instagrain #93: metadata and naming

ebgoldstein, 2022-06-06:
The camera needs some way to record metadata and/or naming of the picture for each session beyond 1,2,3,... 

This is a discussion, and i have some ideas..

jacobstasiewicz, 2022-06-18:
can you explain a little more how I would do this with a hash map, I am currently reading this website https://medium.com/eonian-technologies/file-name-hashing-creating-a-hashed-directory-structure-eabb03aa4091,

ebgoldstein, 2022-06-19:
I'm thinking simpler, where each picture can be 1,2,3,4,.....
but the folder is a random string of letters... and users would then write down the string in their notebook as a key to the location/time/experiment...

(this is a half-way step to users being able to input folder names...)

here is my solution:

```
import random, string

def random_five():
    return ''.join(random.sample(string.ascii_uppercase,5))

FOLDER_NAME = random_five()

```

from https://stackoverflow.com/questions/2823316/generate-a-random-letter-in-python

what do you think @jacobstasiewicz ?

ebgoldstein, 2022-06-20:
this works for me, and i implemented it via ... https://github.com/UNCG-DAISY/SandCam/commit/8af79891deb38718c957fa1bc4e7eb2a9b2389f7

https://github.com/UNCG-DAISY/SandCam/blob/8af79891deb38718c957fa1bc4e7eb2a9b2389f7/software/main_tk.py#L58-L67

to turn it off, you can comment lines 61-63 and 67 and  uncomment line 66

closed 2022-06-20 by ebgoldstein

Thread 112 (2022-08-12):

UNCG-DAISY/Instagrain #112: Where does model perform poorly?

ebgoldstein, 2022-08-12:
It seems to be on the larger sizes for each cumulative class..

dbuscombe-usgs, 2022-08-15:
1. Lighter colored dry sand is overexposed. Imagery is best when grains are darker. 
2. Wet sand is not possible to image due to specular reflection

ebgoldstein, 2022-08-16:
@dbuscombe-usgs I see two things here:
1) your camera has too large of an aperture. Adjusting the camera focus and aperture are analog and manually tuned by the person who builds the camera (me, in the case of your camera). The 'local' fix for you is to close the aperture, and/or reduce the light (which can be done by carefully reducing the numbers in `ringledon.py` https://github.com/UNCG-DAISY/Instagrain/blob/aa72156535290cb7b08d27b3f6a9a3789b64fc78/software/ringledon.py#L5 
The 'global' fix is to write some docs explaining to a camera operator how to do this.. so i made a new issue #116 

2) the ML issue here is to add augmentations in training that can specifically deal with overexposure/underexposure.. that will likely require the albumentations library..

dbuscombe-usgs, 2022-08-16:
Makes sense, although I don't have the ability to log in to the system from my cell phone. Will try to look at aperture etc when i can, but i will prioritize physical samples and (sometimes subpar) photos for now. The variation between dry fine grains and darker grains can exist over tens of metres so not practical to adjust aperture while sampling 

Definitely agree that augmentation and inclusion of subpar imagery are both valuable in the fight against bad data

dbuscombe-usgs, 2022-08-16:
Another thing I may be inadvertently doing in the field is adjusting the focus when putting lens cap on or off. It's difficult to see the screen in bright light and screen condensation (been living in my van and on colder mornings it takes time for the screen to fully clear. Putting this thing through its paces!) so I'm not confident I always spot problems

ebgoldstein, 2022-08-16:
yes, i have worried about this with the lens cap, but i don;t think there is a way to avoid it and i also have not noticed that these small adjustments really influence the focus..
Also, for the record, the current model takes a 1024 x 1024 image and scales it to 224 x 224.. so absolutely perfect focus is likely not needed

ebgoldstein, 2022-08-29:
I updated this issue to reflect the fact that it is for analyzing our current training/val data, not newly collected field data..

ebgoldstein, 2022-08-31:
ok, i am looking at a ranked list of images that have highest error (Summed MAPE across all grain size bins..)
here is an example of images with high error:

[image]
[image]

pics with low error:
[image]

Error is also correlated with larger size fractions, and the range (D98-D2).. here is a list of correlation coefficients for each grain size bin w/ error:
[image]

the high error pics look coarser, and tend to look bimodal.. (note that I did not do a dip test for bimodality, but that could be interesting).. my thinking is that its worth continuing to look for coarser samples, and bimodal samples.. 

for now, i think i will close this issue.. i will make a link to it in the discussion board (since it is really connected to the first release of the model)....

closed 2022-08-31 by ebgoldstein

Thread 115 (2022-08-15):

UNCG-DAISY/Instagrain #115: Increment sample numbers better

dbuscombe-usgs, 2022-08-15:
Sample number goes back to 1 on power up. When sampling in the field, system is sometimes powered off to save battery. Sample numbering system independent of power cycling would be preferable for easier note taking and match-up with physical samples

ebgoldstein, 2022-08-16:
yes, we have discussed this in #96, as well as #102 ..

Essentially, a user needs to be able to reoccupy a folder.. this might be a text box before the program is run?

We also need documentation on this

jacobstasiewicz, 2022-08-26:
fixed with recent commit

ebgoldstein, 2022-08-26:
this is not quite working on my device. I can debug it...

ebgoldstein, 2022-08-31:
ok, i found the issue @jacobstasiewicz : in directories where no pictures exist, there is no `last_line`, so the program fails. 

This is really a corner case - operators should just start a new session/directory in this situation, but its good to know about it... I am not going to write any modifications now, but i will add documentation telling people not to reoccupy empty directories

https://github.com/UNCG-DAISY/Instagrain/blob/21aa04fdc7d24d89b157d10dcb4dd433adad4138/software/main_tk.py#L448-L452

closed 2022-08-31 by ebgoldstein

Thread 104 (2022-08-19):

### ISSUE TITLE
new velcro slot on baseplate

### ISSUE THREAD

**Issue by ebgoldstein** [UNCG-DAISY/Instagrain#104]
It would be nice to have a second velcro slot to secure the GPS wires. My most recent build ended up like this.. 
instead of running the velcro under the whole baseplate, it would be nice if there was just a set of slots.
![IMG_0681](https://user-images.githubusercontent.com/5330599/177182066-3eb4d728-0fff-44d9-9cd6-e83c11697d08.jpg)

**Comment by jacobstasiewicz** [comment]
.stp file in V3 folder

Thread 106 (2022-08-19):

### ISSUE TITLE
New case design

### ISSUE THREAD

**Issue by ebgoldstein** [UNCG-DAISY/Instagrain#106]
I am interested in the design of a new, smaller case.

Some notes:
- goal is to replace the GPS hat with a USB GPS reciever (i.e., the coaxial cable hole on top needs to be USB sized).. removing this hat will also allow a real RTC to be mounted, and for all the other wiring to use jumper cables directly on the RPi GPIO pins.
- remove coral holes on the case - mounts and usb-c hole... (coral can be mounted on a baseplate)
- remove trigger hole
- i really like the peg connection for the tent, and the camera setup, no need to change that. 
- I like the handles (and i even like the specific handles we have), but i woudl be fine with just one, or handle(s) on other sides, or smaller handles, etc.. 
- The 7 inch touchscreen is big, but it is nice, works super well, is easy to setup, and is made by RPi (which makes me think it might have a longer production life). we could find a smaller screen, but it would be nice to work with this size if at all possible...
- The Polycase WQ series, with the hinges are very nice. Would WQ-48 or WQ-50 work? I am also ok if we move to a case w/o hinges, like a WC or WP... (i want to stick with polycase b/c of the CNCing service.

**Comment by jacobstasiewicz** [comment]
The WQ-50 case is what I have already designed and measured. If I remember correctly this is the smallest case I could find that fits everything.

**Comment by ebgoldstein** [comment]
If you remove the handles, can it get smaller (ie, a WP case, which has more size options)?

**Comment by ebgoldstein** [comment]
i guess for the sake of latches, the WQ case is the best...

**Comment by jacobstasiewicz** [comment]
Note: 48 is 2mm to small for the screen, but could be a future option with a different screen size

**Comment by jacobstasiewicz** [comment]
This issue is done, needs to be closed once stp/step files are sent off and approved

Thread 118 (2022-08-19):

UNCG-DAISY/Instagrain #118: While building V3, rewrite v3 instructions and BOM based on changes

ebgoldstein, 2022-08-19:
Notes so far:
- no coral
- USB GPS
- RTC

ebgoldstein, 2022-08-25:
this issue should close with a tagged release (v0.2) and likely also a link to a RPi OS image on zenodo

ebgoldstein, 2022-08-25:
this also might result in upgrading the software to the new RPi OS and the new camera software

jacobstasiewicz, 2022-09-01:
software upgrade is going to be needed for arducam

ebgoldstein, 2022-12-07:
basic instructions are up... mostly copied from v2

ebgoldstein, 2023-03-14:
this should reflect v3 w/ HW cam and v3 w/ autofocus camera

ebgoldstein, 2023-03-21:
ok, i have updated the GH repo and the wiki to reflect:

v1 is 3d printed
v2 is large enclosure
v3 is small enclosure

Software is essentially identical for all of these versions

There are now 2 folders for v3 software: ` v3_HQ` and `v3_auto` - these are substantially different, based on the HQ nad autofocus cameras..

closed 2023-03-21 by ebgoldstein

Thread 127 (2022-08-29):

UNCG-DAISY/Instagrain #127: Test Autofocus Camera

ebgoldstein, 2022-08-29:
Replacing our current camera + lens setup with an autofocus camera module (specifically [the 16MP one from arducam](https://www.arducam.com/docs/cameras-for-raspberry-pi/)) would be easier on an operator b/c there would be no need to deal with focusing (see [wiki docs on focusing](https://github.com/UNCG-DAISY/Instagrain/wiki/Focusing)). 

Additionally, the autofocus camera is less expensive ($30) than the current $75 setup ( HQ cam ($50) + Lens ($25) )

Previous experiments with the current setup suggest the 1024x1024 center crop used for ML is ~32mm x ~32mm. see: https://github.com/UNCG-DAISY/Instagrain/issues/33#issuecomment-940111636. This should be retested with the current v2 camera, results posted here..

Note that the current ML model works with a 1024 x 1024 center crop that is downscaled to 224 x 224 and then run through the network. 

To incorporate the autofocus camera, our constraints are:
1. image atleast a ~32mm x 32mm area. 
2. reduce distortion (so maybe another center crop will be necessary, (so the total image size would be much larger than 32 mm x 32mm, just like how it is now)
3. be atleast 224 x 224 pixels (larger is better - i would aim for 512 x 512.. 
4. Make sure that (fine) sand sized grains are visible and more than a single pixel..

To accomplish this, there will need to be some experimentation with the camera - adjusting distance - with some way to measure the size of the imaging surface (graph paper/rulers/scales)...

This issue is setup to track this project, post pictures from the autofocus camera, and decide whether it should be incorporated into future builds. There are 3 action items:

- [ ] Measure image area with original camera, and make a new measurement for the cropped imaging area
- [ ] Attach autofocus camera and get it working
- [ ] Determine if the 4 constraints listed above can be met, and record the Camera Tent size that is needed

If the tests look promising, there will be two future issues to make:
1.  a new camera tent will need to be made to enforce the correct distance between end of tent and camera,
2.  code changes will be needed in `main_tk.py`

ebgoldstein, 2022-09-02:
as mentioned here: https://github.com/UNCG-DAISY/Instagrain/issues/118#issuecomment-1234559910, RPiOS will need an update to work with the arducam

ebgoldstein, 2022-09-08:
docs for autofocus camera: https://www.arducam.com/raspberry-pi-camera/autofocus/

jacobstasiewicz, 2022-09-14:
I can confirm the cropped image is roughly 32x32 +/- 1mm 
[image]
[image]

ebgoldstein, 2022-09-14:
how far off the bed/imaging surface is this?

jacobstasiewicz, 2022-09-14:
The new camera is attached and working in bullseye but only via shell, I have been battling some demons trying to get it working right on python. I will update you on progress. I think I downloaded a janky package somewhere along the line.

jacobstasiewicz, 2022-09-14:
1. I will have to measure once I get into the lab, but im going to look through my notes quickly and see if I wrote it down.

2. How would I go about finding this out?

ebgoldstein, 2022-09-14:
the easiest way to see the # of pixels is just with the RPi desktop environment. navigate to the picture, right click on it, go down to properties, and then look at the image tab... when i did it on the zoom above it is 1024 x 1024 pixels... (but if you could do it on the RPi just to check, that would be good.

ebgoldstein, 2022-09-14:
ok cool - i have confidence that we will get it working with python.. 

i suggest that you design/scale a tent that is the correct distance off the bed, and then print it.. this could be printed with cheaper resin (draft, or normal grey/black/white.. i have these)... 

then we can build a new autofocus camera as a dev. machine to get the python code working..

thoughts?

jacobstasiewicz, 2022-09-14:
Yes that sounds good

ebgoldstein, 2022-09-14:
i made 2 new issues (#131 and #132).. we can close this for now since the testing is done.

jacobstasiewicz, 2022-09-20:
off initial test I think this camera will need to be farther away from the bed than the recent, for example her is an image taken at roughly 76 mm form the bed (lense to bed) vs 72mm for V2)
[image]
The image size in pixels is 4656x3496
Changing the resolution to 2048x2048 here is the resulting picture
[image]

jacobstasiewicz, 2022-09-20:
This leads to three questions I have.
1. Since the camera has no major lenses distortion do we need a crop?
2. If I can find the right area for the auto focus camera do we need to crop down to 1024x1024 pixels. I know more pixels would be better for the model but not the quanitzation/speed. (question is can you explain how the model would change if we used larger images)
3. I have been using resolution and # of pixels interchangeably, but I know in larger  displays it means two different things. Is my analysis right or have I used them the wrong way for this example.

ebgoldstein, 2022-09-20:
Ok.. nice work...

so, naively, the goal is to make a 1024 x1024 image that is 32mm x 32mm to be harmonized with the other camera and therefore the existing model. Note that the model uses the 1024x1024 images, but rescaled to 224x224... images that are 1024 x 1024 are just too big for an on-device model... 
(see code block 5 [here](https://github.com/UNCG-DAISY/Instagrain/blob/main/ML/src/Instagrain-MAPE-MNv2-Aug_27_QAT.ipynb)): 

```
#set color
c_ch = 3
c_mode = 'rgb'

#set Image size (RGB so imshape is 3)
pix_dim = 224
imsize = (pix_dim, pix_dim) 
imshape = (pix_dim, pix_dim, c_ch)
```

so, for the autofocus, there are two options:
- we get to this 32mm x 32mm == 1024px x 1024px  with hardware (via a different sized lens tent)
- we get there with software. (via some image operations)

i propose that we get there with software... so, if you use the lens tent that we have, then in the code we do something like this:

- center_crop the image to a 32mm x 32mm size
- resize it to 1024x1024 pixels

the only check i want to make is just to make sure that the cropped image is bigger than 1024x1024...

ALSO - we still want to save the fill size image.. they might be useful later when working with bigger grain sizes...

does this make sense?

ebgoldstein, 2022-09-20:
With this new plan, i proposae we close this issue (since we have a path forward)... 
also this means that #131 can be closed.. 
and these software changes mentioned above can be implemented in #132

closed 2022-09-20 by ebgoldstein

jacobstasiewicz, 2022-09-20:
sounds good

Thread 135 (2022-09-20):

UNCG-DAISY/Instagrain #135: Parts for dev work

ebgoldstein, 2022-09-20:
In the course of discussing a 'dev camera', it turns out we just need a simple way to prototype cameras and do development work that do not rely on having an actual enclosure...

the RPi can be attached to the RPI screen (with the included standoffs).. and then we just need like a plate that can attach to the hood (w/ peg holes) and then holes for the camera standoff stuff...

_Originally posted by @ebgoldstein in https://github.com/UNCG-DAISY/Instagrain/issues/133#issuecomment-1252577400_

ebgoldstein, 2022-09-21:
via @jacobstasiewicz 

"has raspberry pi on left, battery slots on right, button on top, camera mounting holes, and the peg holes for the hood.. little 5mm  bumps on the bottom for when the hood or camera are not on"

[image]
[image]

jacobstasiewicz, 2022-10-05:
Added file to github

closed 2022-10-05 by jacobstasiewicz

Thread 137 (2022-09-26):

UNCG-DAISY/Instagrain #137: New RPi image

ebgoldstein, 2022-09-26:
Make a new RPi image for v2 camera, with new model.. might require a pip udpate and a new TF interpreter version

ebgoldstein, 2022-09-27:
https://www.tomshardware.com/how-to/back-up-raspberry-pi-as-disk-image

https://magpi.raspberrypi.com/articles/back-up-raspberry-pi

ebgoldstein, 2022-09-27:
this is done.. still thinking about how to shrink it and serve it

ebgoldstein, 2022-09-27:
the image is 32 GB. A `.tar.xz` is 1.2GB..

ebgoldstein, 2022-09-27:
I tested writing the image on a 32GB SD card using the Rsaaspberry Pi imager.  It worked (:tada: ).
@jacobstasiewicz, i will send you a link to the image, and ask that you test it too..

ebgoldstein, 2022-09-29:
ok, it seems to be working.. I need to put it on Zenodo and then close this issue...

WFarebrother, 2022-11-14:
@ebgoldstein If possible, can I please get a copy of the image to test? Currently attempting to put a V2 device together. Thanks!

ebgoldstein, 2022-11-14:
@WFarebrother - here is a google drive link for the v2 image: https://drive.google.com/file/d/1Vkpmd04zKXRPN8tuaD6aKBoAVZ30dl68/view?usp=sharing

please let me know how you get on! and feel free to reach out if you want to discuss further!

(I am going to close this issue for now, and wait for a full zenodo release until after some testing, etc.....)

closed 2022-11-14 by ebgoldstein

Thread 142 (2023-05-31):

### ISSUE TITLE
Case Improvements

### ISSUE THREAD

**Issue by jacobstasiewicz** [UNCG-DAISY/Instagrain#142]
- [ ] fix handle cutout diameters
- [ ] baseplate cutout for handle screw ends
- [ ] one boss removed for velcro cutout
- [ ] brainstorm camera connection ideas
- [ ] any other ideas to make it easier to build (i.e., wiring the camera light to the Pi)

**Comment by ebgoldstein** [comment]
i think these are non-essential at this time, so i am closing

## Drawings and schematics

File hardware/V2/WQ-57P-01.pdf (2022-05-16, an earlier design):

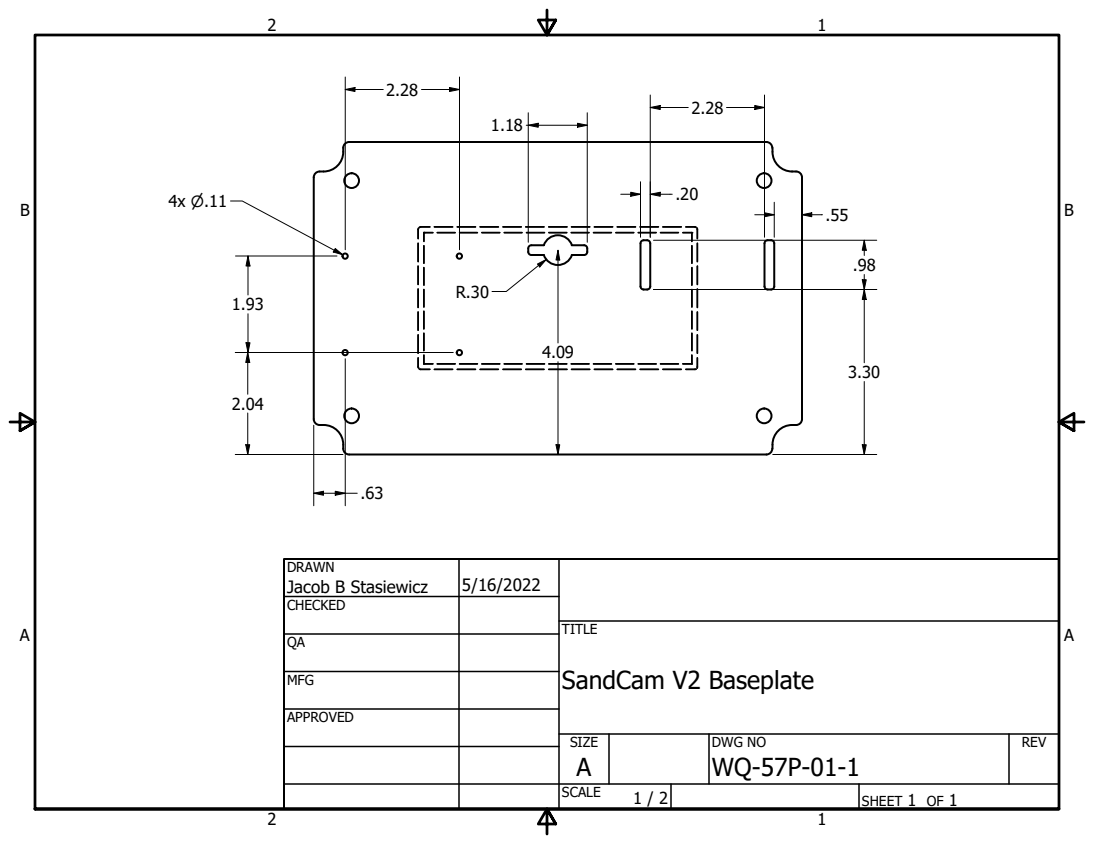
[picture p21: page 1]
SandCam V2 Baseplate

DRAWN Jacob B Stasiewicz | 5/16/2022

CHECKED

MFG

APPROVED

SIZE A | DWG NO WQ-57P-01-1 | REV

SCALE 1 / 2 | | SHEET 1 OF 1

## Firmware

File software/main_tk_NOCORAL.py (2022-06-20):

# Written by Jacob Stasiewicz and Evan Goldstein
#
# MIT License

#import packages
from gpiozero import Button, LED
from picamera import PiCamera
import gpsd
import os
import glob
import datetime
import subprocess
#from PIL import Image#, ImageTk
from PIL import ImageTk, Image
import PIL.Image
import numpy as np
import pandas as pd

#import TF
from tflite_runtime.interpreter import Interpreter

#Import tk Packages 
import time
from time import sleep 
from time import strftime
from tkinter import *
import tkinter as tk
#Import NeoPixel Commands
import board
import neopixel
import random, string
#Import matplotlib
import matplotlib as mpl
import matplotlib.pyplot as plt

#software version 
software_version = 0.1
model_version = 0.1

#define gpio pins and variables
pwd = os.getcwd()
camera = PiCamera()
camera.resolution = (2048,2048)
counter = 1

#New GPS trial
gpsd.connect()

#TFLITE model, not the coral one
path_to_model = "./models/SandCam_MNv2_QAT_notdense.tflite"

# Initialize the TF interpreter
interpreter = Interpreter(path_to_model)
interpreter.allocate_tensors()
#uncomment lines below to debug and look at expected I/O
#print(interpreter.get_input_details())
#print(interpreter.get_output_details())

#make new directory and create text file within
#random 5 letter generation fn
def random_five():
	return ''.join(random.sample(string.ascii_uppercase,5))

#direcname = str(input("name your file: "))
time = datetime.datetime.now()
#direcname = time.strftime("%m_%d_%Y_%H_%M_%S")
direcname = random_five()
newpath = "/home/pi/Documents/sand_cam/data" + '/' + direcname
croppath = "/home/pi/Documents/sand_cam/data" + '/' + direcname + '/crop'
plotpath = "/home/pi/Documents/sand_cam/data" + '/' + direcname + '/plot'
os.makedirs(newpath)
os.makedirs(croppath)
os.makedirs(plotpath)

print("Made a Directory for this session:")
print(newpath)

txtfile = open(newpath + '/' + direcname + '.csv', 'w+')
txtfile.write('software_version ' + str(software_version) + ',' +  'model-version ' + str(model_version) + "\n")
txtfile.write('Filename, Date/Time (UTC), Latitude (DD) , Longitude (DD), Altitude(m), D_2(mm), D_5(mm), D_10(mm), D_16(mm), D_25(mm), D_50(mm), D_75(mm), D_84(mm), D_90(mm), D_95(mm), D_98(mm) '"\n")
txtfile.close()
textarg = str(newpath + '/' + direcname + '.csv')
croparg = str(croppath)

print("Made a txt file for this session")

#define functions
def capture():
	global counter 
	global lat1 
	global lon1 
	global alt1
	#get GNSS data
	report = gpsd.get_current()
	lat1 = "-9999"
	lon1 = "-9999"
	alt1 = "-9999"
	time = "na"
	print(report)
	if getattr(report,'lat',0.0)!=0:
		lat1 = str(getattr(report,'lat',0.0))
	if getattr(report,'lon',0.0)!=0:
		lon1 = str(getattr(report,'lon',0.0))
	if getattr(report,'alt','nan')!= 'nan':
		alt1 = str(getattr(report,'alt','nan'))
	if getattr(report,'time','nan')!= 'nan':
		time = str(getattr(report,'time','nan'))
	sleep(2)
	camera.capture(newpath + '/' + str(counter) + '.jpg')
	im = PIL.Image.open(str(newpath + '/' + str(counter) + '.jpg'))
	crop_img = crop_center(im,1024,1024)
	crop_img.save(croppath + '/crop' + str(counter) + '.jpg')
	txtfile = open(newpath + '/' + direcname + '.csv', 'a')
	txtfile.write( str(counter) + ',' + str(time) +
	',' + lat1 + ',' + lon1 + ','+ alt1 + ',')
	txtfile.close()
	
	print(lat1)
	print(lon1)
	print(alt1)
	
	#prediction step
	#with pyDGS
	#pyDGS()
	#with TFLite:
	
	TFlitePred(crop_img)
	print('that was picture:')
	print(counter)
	counter = counter + 1

def previewon():
	camera.start_preview()
	subprocess.call(["./ringledon.sh"])
	
def previewoff():
	camera.stop_preview()
	subprocess.call(["./ringledoff.sh"])
	
def crop_center(pil_img, crop_width, crop_height):
   img_width, img_height = pil_img.size
   return pil_img.crop(((img_width - crop_width) // 2,
                          (img_height - crop_height) // 2,
                          (img_width + crop_width) // 2,
                          (img_height + crop_height) // 2))
                          
def pyDGS():
	global textarg 
	list_of_files_crop = glob.glob(croppath + '/*.jpg')
	latest_file_crop = str(max(list_of_files_crop, key=os.path.getctime))
	print("using pyDGS to get grain size")
	subprocess.call(["python3", "example_test.py", latest_file_crop, textarg])
	print("ready for next picture")

def TFlitePred(crop_img):
    #get image in the correct shape,size, format
    crop_img = crop_img.resize((224,224))
    converted_crop = np.array(crop_img, dtype=np.float32)
    r_crop_img = converted_crop/255
    crop_img_exp = np.expand_dims(r_crop_img, axis=0)

    input_index = interpreter.get_input_details()[0]["index"]
    output_index = interpreter.get_output_details()[0]["index"]
    interpreter.set_tensor(input_index, crop_img_exp)
    interpreter.invoke()
    predictions = interpreter.get_tensor(output_index)

    
    global predictionstk

    predictionstk = predictions.tolist()
    predictionstk = [round(num,3) for num in predictionstk[0]]
    print(predictions)
    
    stats = pd.DataFrame(predictions)
    statsrounded = stats.round(decimals=3)
    statsrounded.to_csv(textarg, mode='a', header = False, index = False)
    return predictions
    	
grain_sizes_label= ["D_2(mm) ", "D_5(mm) ", "D_10(mm)", "D_16(mm)", "D_25(mm)", "D_50(mm)", "D_75(mm)", "D_84(mm)", "D_90(mm)", "D_95(mm)", "D_98(mm)"]  
def stats_update():
	stats.delete(0,END)
	for i in range(0,len(grain_sizes_label)):
		stats.insert(i, str(grain_sizes_label[i]) + ": " + str(predictionstk[i]))
		#stats.update()
		
def make_plt():
	x = predictionstk
	cdf = [.02,.05,.10,.16,.25,.50,.75,.84,.90,.95,.98]
	pdf = np.gradient(cdf)
	
	#cdf
	fig, ax = plt.subplots(figsize=(4.5,5.5), dpi=35)
	ax.plot(x,cdf, color="green", linewidth = 2)
	plt.grid()
	plt.xticks(size = 16)
	plt.yticks(size = 16)
	plt.title("CDF Sample " + str(counter-1), fontsize = 16, fontweight = "bold" )
	ax.tick_params(axis="x", rotation = 50)
	ax.set_xlim([min(x), max(x)])
	ax.set_ylim([0, 1])
	fig.savefig(plotpath + "/" + "figure_cdf" + str(counter-1) + ".png")
	
	#pdf
	fig, ax = plt.subplots(figsize=(4.5,5.5), dpi=35)
	ax.plot(x,pdf, color="red", linewidth = 2)
	plt.grid()
	plt.xticks(size = 16)
	plt.yticks(size = 16)
	plt.title("PDF Sample " + str(counter-1), fontsize = 16, fontweight = "bold" )
	ax.tick_params(axis="x", rotation = 50)
	ax.set_xlim([min(x), max(x)])
	ax.set_ylim([0, 1])
	fig.savefig(plotpath + "/" + "figure_pdf" + str(counter-1) + ".png")
	
current_plt = 1 
	
def change_plt():
	global current_plt
	if current_plt == 1:
		current_plt = 0
	else:
		current_plt = 1
	plot_update()
	
def plot_update():
	global grainplot
	if current_plt == 1:
		plotfile = plotpath + "/" + "figure_cdf" + str(counter-1) + ".png"
		grainplot = tk.PhotoImage(file=plotfile)
		statsplot = tk.Button(master, image=grainplot, command=change_plt)
		statsplot.place(relheight=0.508, width=listsize , x=listplace, rely=0.098)
		statsplot.update()
	else:
		plotfile = plotpath + "/" + "figure_pdf" + str(counter-1) + ".png"
		grainplot = tk.PhotoImage(file=plotfile)
		statsplot = tk.Button(master, image=grainplot, command=change_plt)
		statsplot.place(relheight=0.508, width=listsize , x=listplace, rely=0.098)
		statsplot.update()
	
def photo_update():
	#place image on screen
	global img3
	sandimage = newpath + '/' + str(counter-1) + '.jpg'
	img1 = PIL.Image.open(sandimage) #counter minus 1 because image hasnt been taken yet 
	previewsize = screen_height - (screen_height*0.10) #this creates the maximum square size we can have in the middle of the screen
	img2 = img1.resize((int(previewsize),int(previewsize)))
	img3 = ImageTk.PhotoImage(img2)
	preview = Label(master, image=img3)
	preview.place(height=previewsize, width=previewsize, relx=0.216, rely=0.02) #to fix so that no matter what it is square
	preview.update()
		
#Update gui function
def updategui():
	stats_update()
	coord_update()
	photo_update()
	make_plt()
	plot_update()

#Capture + update gui
def capturegui():
	subprocess.call(["./ringledon.sh"])
	capture()
	subprocess.call(["./ringledoff.sh"])
	#make_plt()
	updategui()

#preview on/off
def preview():
	previewon()
	sleep(5)
	previewoff()

def coord_update():
	lattk = Label(master, text = "Latitude (DD): " +"\n"+ str(lat1), borderwidth=1, relief="solid",font = ("Consolas", 10))
	lattk.place(relheight=0.123, relwidth=0.176, relx=0.02, rely=0.608)
	lattk.update() #would it be better to make this global or put it in the capture function
	lontk = Label(master, text = "Longitude (DD): " +"\n"+ str(lon1), borderwidth=1, relief="solid",font = ("Consolas", 10))
	lontk.place(relheight=0.123, relwidth=0.176, relx=0.02, rely=0.731)
	lontk.update()
	elevtk = Label(master, text = "Altitude (m): " +"\n"+ str(alt1), borderwidth=1, relief="solid",font = ("Consolas", 10))
	elevtk.place(relheight=0.123, relwidth=0.176, relx=0.02, rely=0.854)
	elevtk.update()

### BELOW IS TKINTER CODE ###

#create main window

master = tk.Tk()

#screen height and width

screen_width = master.winfo_screenwidth()
screen_height = master.winfo_screenheight()
print(screen_width)
print(screen_height)
master.geometry(str(screen_width)+'x'+str(screen_height))

#make title
master.title('SandCam')

#make buttons
previewbutton = tk.Button(master, text="Preview", font = ("Consolas", 22), command=preview,background='yellow') #uncomment
previewbutton.place(relheight=0.176, relwidth=0.176, relx=0.02, rely=0.216) 

shutterbutton = tk.Button(master, text="Capture", font = ("Consolas", 22), command=capturegui,background='green') #uncomment
shutterbutton.place(relheight=0.176, relwidth=0.176, relx=0.02, rely=0.412) 

#make labels
sandcam = Label(master, text = "Sandcam", borderwidth=1, relief="solid", font = ("Consolas", 22))
sandcam.place(relheight=0.176, relwidth=0.176, relx=0.02, rely=0.02)

# latestfile = Label(master, text = "last file", borderwidth=1, relief="solid")
# latestfile.place(relheight=0.176, relwidth=0.176, relx=0.02, rely=0.608)

lattk = Label(master, text = "Latitude (DD): ", borderwidth=1, relief="solid",font = ("Consolas", 10))
lattk.place(relheight=0.123, relwidth=0.176, relx=0.02, rely=0.608)

lontk = Label(master, text = "Longitude (DD): ", borderwidth=1, relief="solid",font = ("Consolas", 10))
lontk.place(relheight=0.123, relwidth=0.176, relx=0.02, rely=0.731)

elevtk = Label(master, text = "Altitude (m): ", borderwidth=1, relief="solid",font = ("Consolas", 10))
elevtk.place(relheight=0.123, relwidth=0.176, relx=0.02, rely=0.854)

##create height variable
previewsize = screen_height- (screen_height*0.10)
print(previewsize)
preview = Label(master, text = "Sandcam", borderwidth=1, relief="solid")
preview.place(height=previewsize, width=previewsize, relx=0.216, rely=0.02) #to fix so that no matter what it is square

#make ListBox
##create variable
listsize = screen_width - (previewsize + (.08*screen_width) + (screen_width*0.176))
listplace = (previewsize + (.06*screen_width) + (screen_width*0.176))

#
#make clock
def time():
    string = strftime('%H:%M:%S')
    lbl.config(text = string)
    lbl.after(1000, time)
    
lbl = Label(master, font = ('Consolas', 15, 'bold'),
            background = 'black',
            foreground = 'green')
lbl.place(x=listplace, rely=0.02, relheight=0.058, width=listsize)

#graph
stats = tk.Listbox(master, borderwidth=1, relief="solid", font = ("Consolas", 8))
stats.place(relheight=(1-0.648), width=listsize , x=listplace, rely=0.628)

time() 

#create
while True:
	master.mainloop()

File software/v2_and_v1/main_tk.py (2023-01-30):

# Written by Jacob Stasiewicz and Evan Goldstein
# MIT License

#import packages
import time, random, string
#start_time = time.time()
from time import sleep 
from picamera import PiCamera
import gpsd
import os, subprocess
from PIL import ImageTk
import PIL.Image
import numpy as np
import pandas as pd
from scipy import interpolate
import matplotlib.pyplot as plt
from tkinter import *
import tkinter as tk
from tflite_runtime.interpreter import Interpreter
#stop_time = print("importing packages : " + str(time.time() - start_time))

#DEFINE SOFTWARE VERSIONS
software_version = 0.21
model_version = 0.2

#SET UP CAMERA
#start_time = time.time()
pwd = os.getcwd()
camera = PiCamera()
camera.resolution = (2048,2048)
#stop_time = print("defining pins and vars: " + str(time.time() - start_time))

#GPSD_CONNECT
#start_time = time.time()
gpsd.connect()
#stop_time = print("GPS connect: " + str(time.time() - start_time))

#SET UP TF MODEL
#start_time = time.time()
path_to_model = "./models/SandCam_MNv2_QAT_notdense_aug27.tflite"
interpreter = Interpreter(path_to_model)
interpreter.allocate_tensors()
#uncomment lines below to debug and look at expected I/O
#print(interpreter.get_input_details())
#print(interpreter.get_output_details())
#stop_time = print("TFLITE_stuff: " + str(time.time() - start_time))

#make new directory and create text file within
#random 5 letter generation fn
def random_five():
    return ''.join(random.sample(string.ascii_uppercase,5))

### DEFINE THE FUNCTIONS ###

global counter 


counter = 0

#start_time = time.time()
def capture():
    global counter
    counter = counter + 1
    #get GNSS data
    global lat1
    global lon1
    global elev1
    lat1 = "-9999"
    lon1 = "-9999"
    elev1 = "-9999"
    time = "na"
    report = gpsd.get_current()

    print(report)
    if getattr(report,'lat',0.0)!=0:
        lat1 = str(getattr(report,'lat',0.0))
    if getattr(report,'lon',0.0)!=0:
        lon1 = str(getattr(report,'lon',0.0))
    if getattr(report,'elev','nan')!= 'nan':
        elev1 = str(getattr(report,'elev','nan'))
    if getattr(report,'time','nan')!= 'nan':
        time = str(getattr(report,'time','nan'))
    #sleep(2)
    camera.capture(newpath + '/' + str(counter) + '.jpg')
    im = PIL.Image.open(str(newpath + '/' + str(counter) + '.jpg'))
    crop_img = crop_center(im,1024,1024)
    crop_img.save(croppath + '/crop' + str(counter) + '.jpg')
    txtfile = open(newpath + '/' + direcname + '.csv', 'a')
    txtfile.write( str(counter) + ',' + str(time) +
    ',' + lat1 + ',' + lon1 + ','+ elev1 + ',')
    txtfile.close()
    
    print(lat1)
    print(lon1)
    print(elev1)
    
    TFlitePred(crop_img)
    print('that was picture:')
    print(counter)
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

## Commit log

2021-05-21 Create photosieve.py
    Main script for controlling camera, gps, RTC, and lled
2021-06-08 Delete sediformat.csv
    switched values
    [sediformat.csv]
2021-06-09 Added code to control LED ring light
2021-06-09 Files to control Led light
    ALL files must be in the same folder
2021-06-14 ring light mount
    [sedinetcam.iam]
2021-06-14 led ring mount
    [lightmount.ipt]
2021-10-11 set camera res; pixel color fix
    [Olympus_Mons_Dunes.csv]
2021-10-20 add new GNSS board (#42)
2021-10-24 added buttons and powerbank
2021-11-11 🍾🍾 ML is on the camera 🍾🍾
2021-11-11 still 🍾🍾
2022-03-18 reorg `/hardware`
    [SediNetCamv2.fzz, battery_case.stl, body_sedicamsmallerv2.stl, lightmount.stl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]
2022-03-23 filtered some links
    [BOMv2.csv]
2022-05-18 Had to change something, it fit but not how I wanted it to
    [ledmountv2.stl]
2022-06-08 updating to new .stl file
    [focuscover.stl]
2022-06-08 focus cover v3, added ring at bottom. Will 100% be stronger
    [focuscover.stl]
2022-07-04 new main file: just TFLite, not coral
    Coral edgeTPU remains out-of-stock. This Main file switches over to using the normal TFLite runtime, and the non-coral model file. Speed is only marginally compromised. Lets use this as the main on-d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
2022-08-19 BOMv3, new folder name
    [BOMv3.csv, Camcover.stl, WQ-50_BASEPLATE.stp, WQ-50_BODY.stp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]
2022-08-20 rm GPS hat+antenna
    [BOMv3.csv]
2022-08-21 add GPS USB
    [BOMv3.csv]
2022-10-05 Added dev plate .stl file
    [dev_platev2.stl]
2022-12-26 Updated for bullseye
    Updated the preview window to close and open, consolidated 3 preview functions to 1
    Updated GPSD to work, see note I sent
    Added camera.stop() to work
    Changed some instances of sandcam in the gui to instagrain
2023-03-16 capture is working
    also the resolution is set to 2048 for full mages and 1024 for crops.. the 1024 crop are essentially identical to 1024 crops using the v2 camers (w/ HQ lens) - 32mm
2023-03-23 update BOMv3
    [BOMv3.csv]
2023-06-01 Case Improvements
    [WQ-50P_BASEPLATE.stp, WQ-50_BODY.stp]
2023-06-06 adjusted mushroom peg diameter
    [cam_cover.stl]
